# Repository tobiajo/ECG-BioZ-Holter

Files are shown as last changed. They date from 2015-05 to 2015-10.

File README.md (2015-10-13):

# ECG/BioZ Holter (c) by Tobias Johansson

Design and development of a pocket-sized ECG device with respiration monitoring, accelerometer and gyroscope. The produced prototype transmits sampled data with a MCU (PIC24) over Bluetooth to an Android device for which a simple app was developed. To achieve the objective; a system solution was engineered, components chose, PCB designed, soldering done and components programmed or configured.

## Main components

- Texas Instruments ADS1292R
- InvenSense MPU-6050
- Microchip PIC24FJ64GA002
- HC-05 Bluetooth Module

## System overview



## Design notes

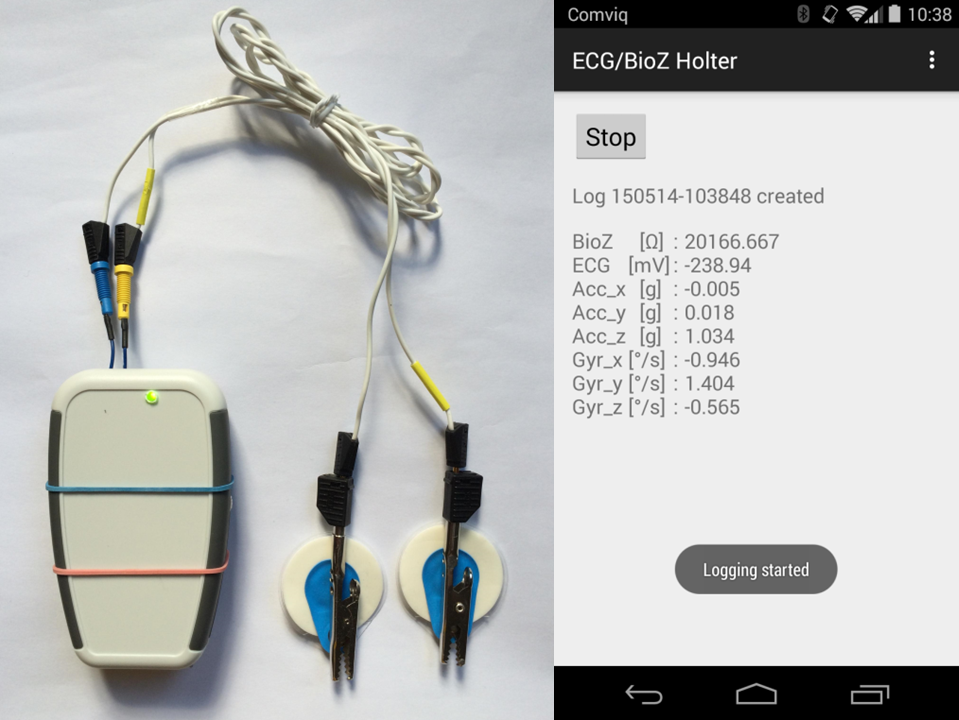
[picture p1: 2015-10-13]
device-and-app.png

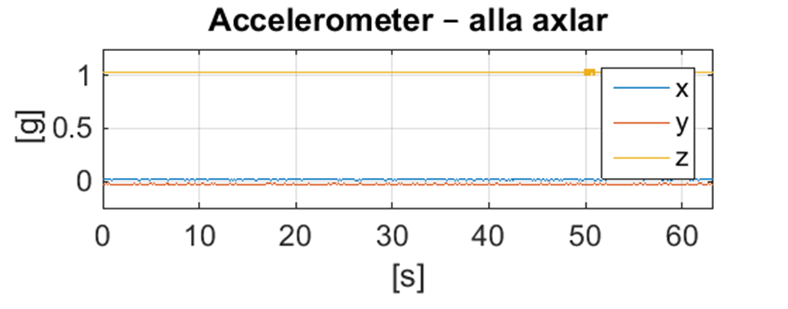
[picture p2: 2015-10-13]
output-plot-accelerometer-fixed.png

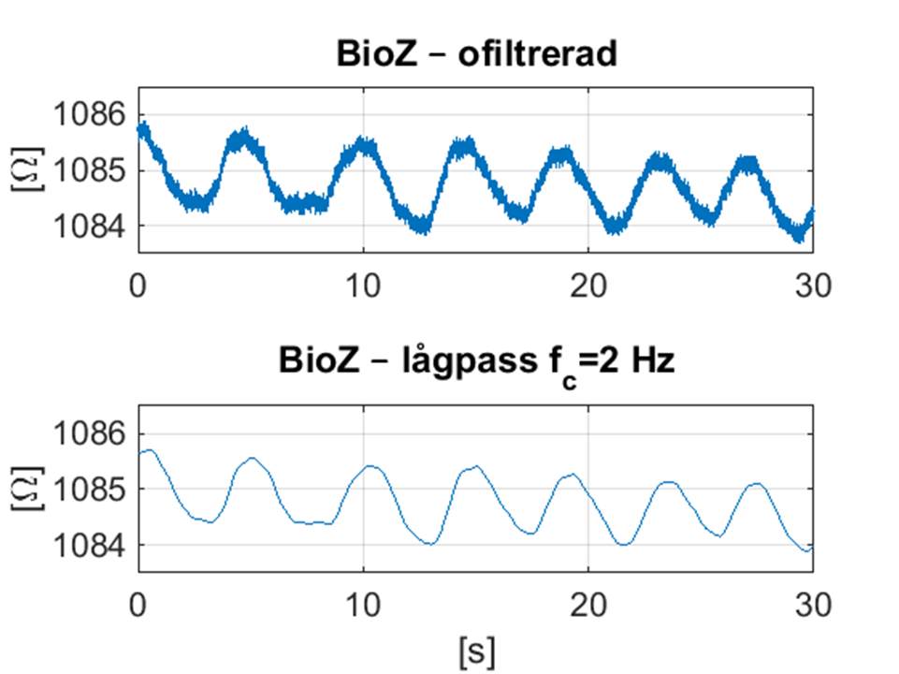
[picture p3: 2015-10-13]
output-plot-respiration-person.png

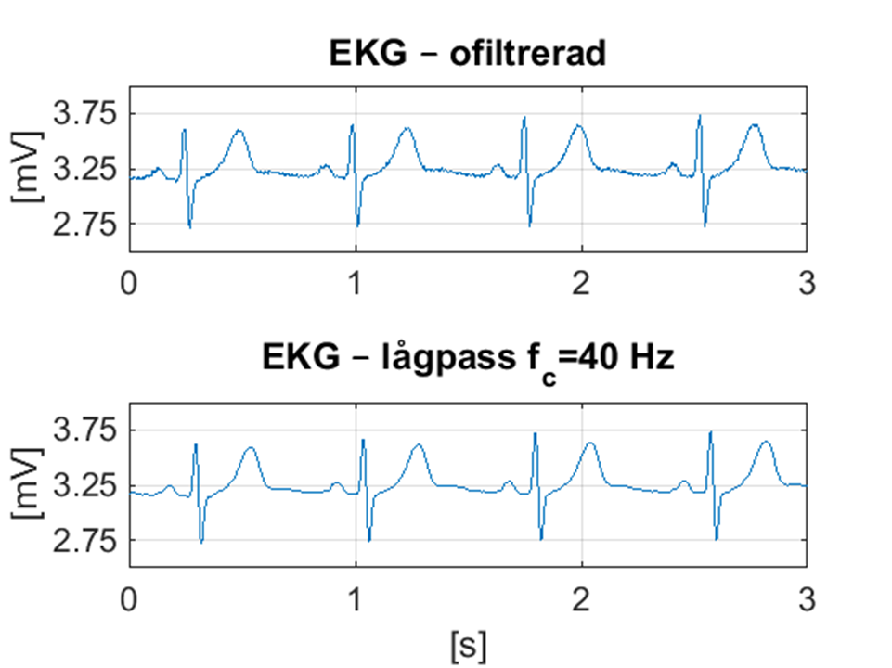
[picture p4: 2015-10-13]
output-plot-ecg-person.png

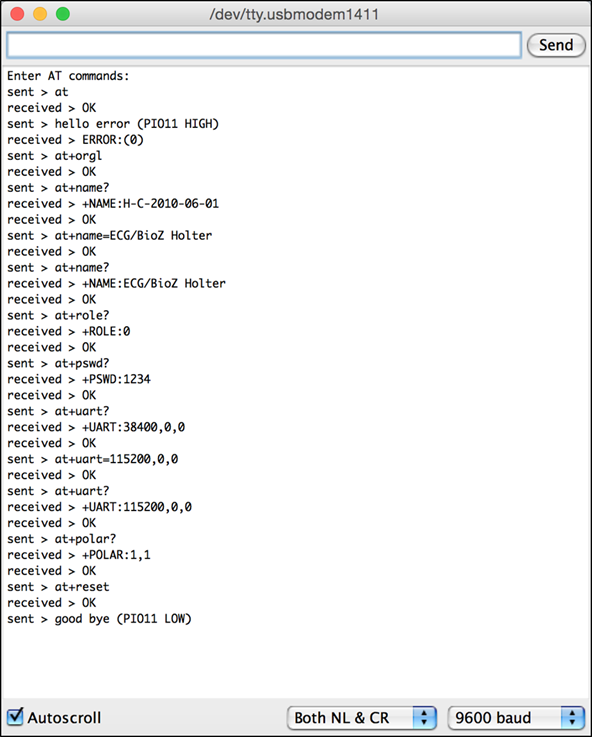
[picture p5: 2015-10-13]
Bluetooth/Arduino/ATSerialMonitorHC05/arduino-config.png

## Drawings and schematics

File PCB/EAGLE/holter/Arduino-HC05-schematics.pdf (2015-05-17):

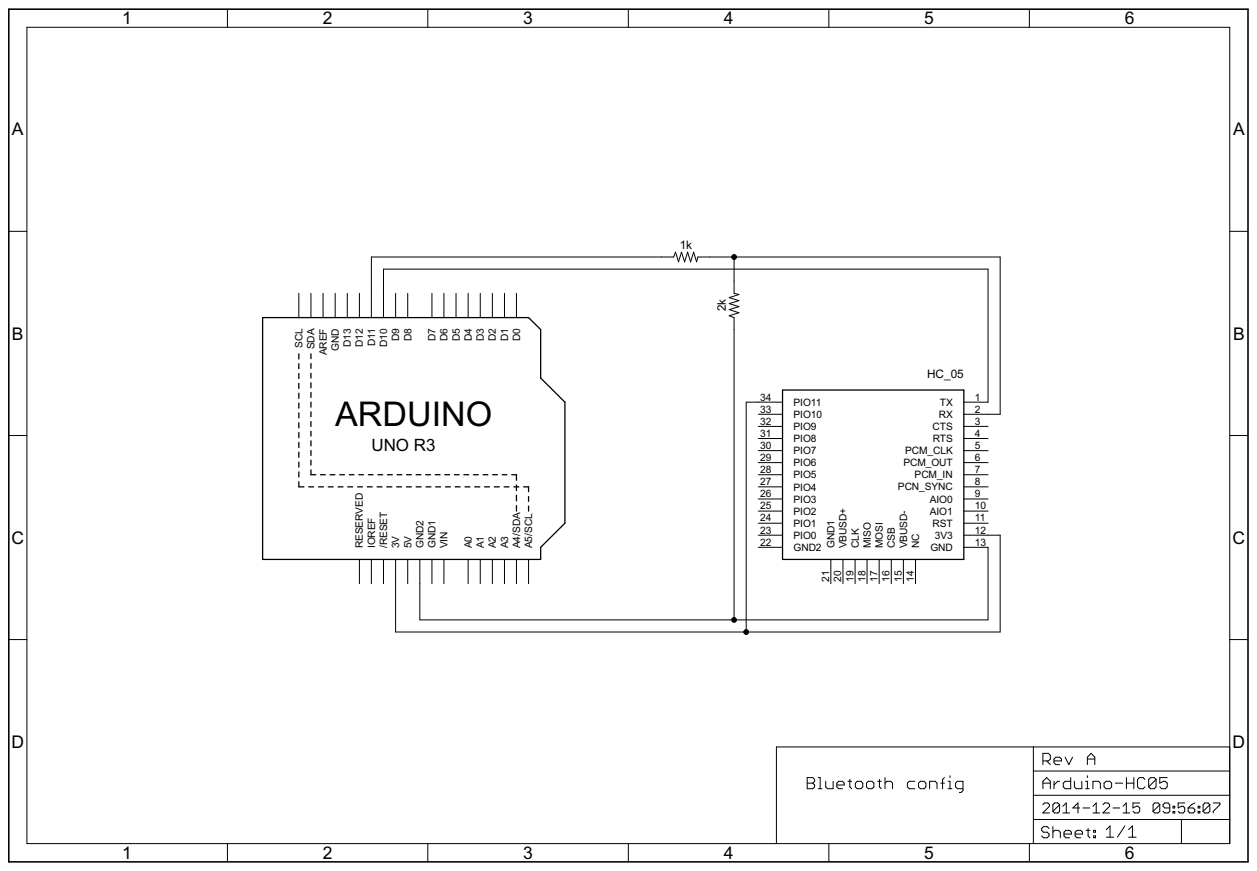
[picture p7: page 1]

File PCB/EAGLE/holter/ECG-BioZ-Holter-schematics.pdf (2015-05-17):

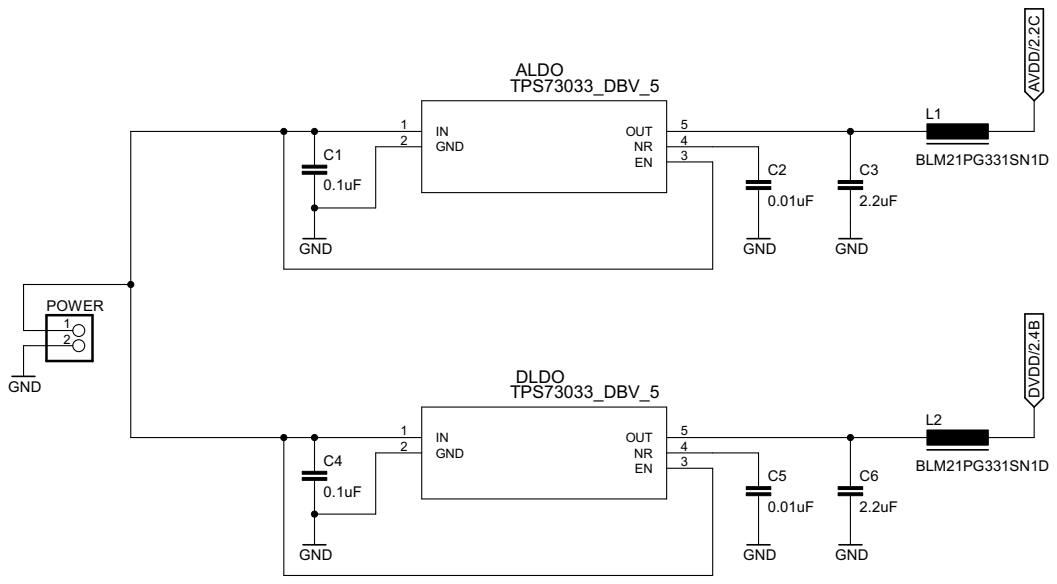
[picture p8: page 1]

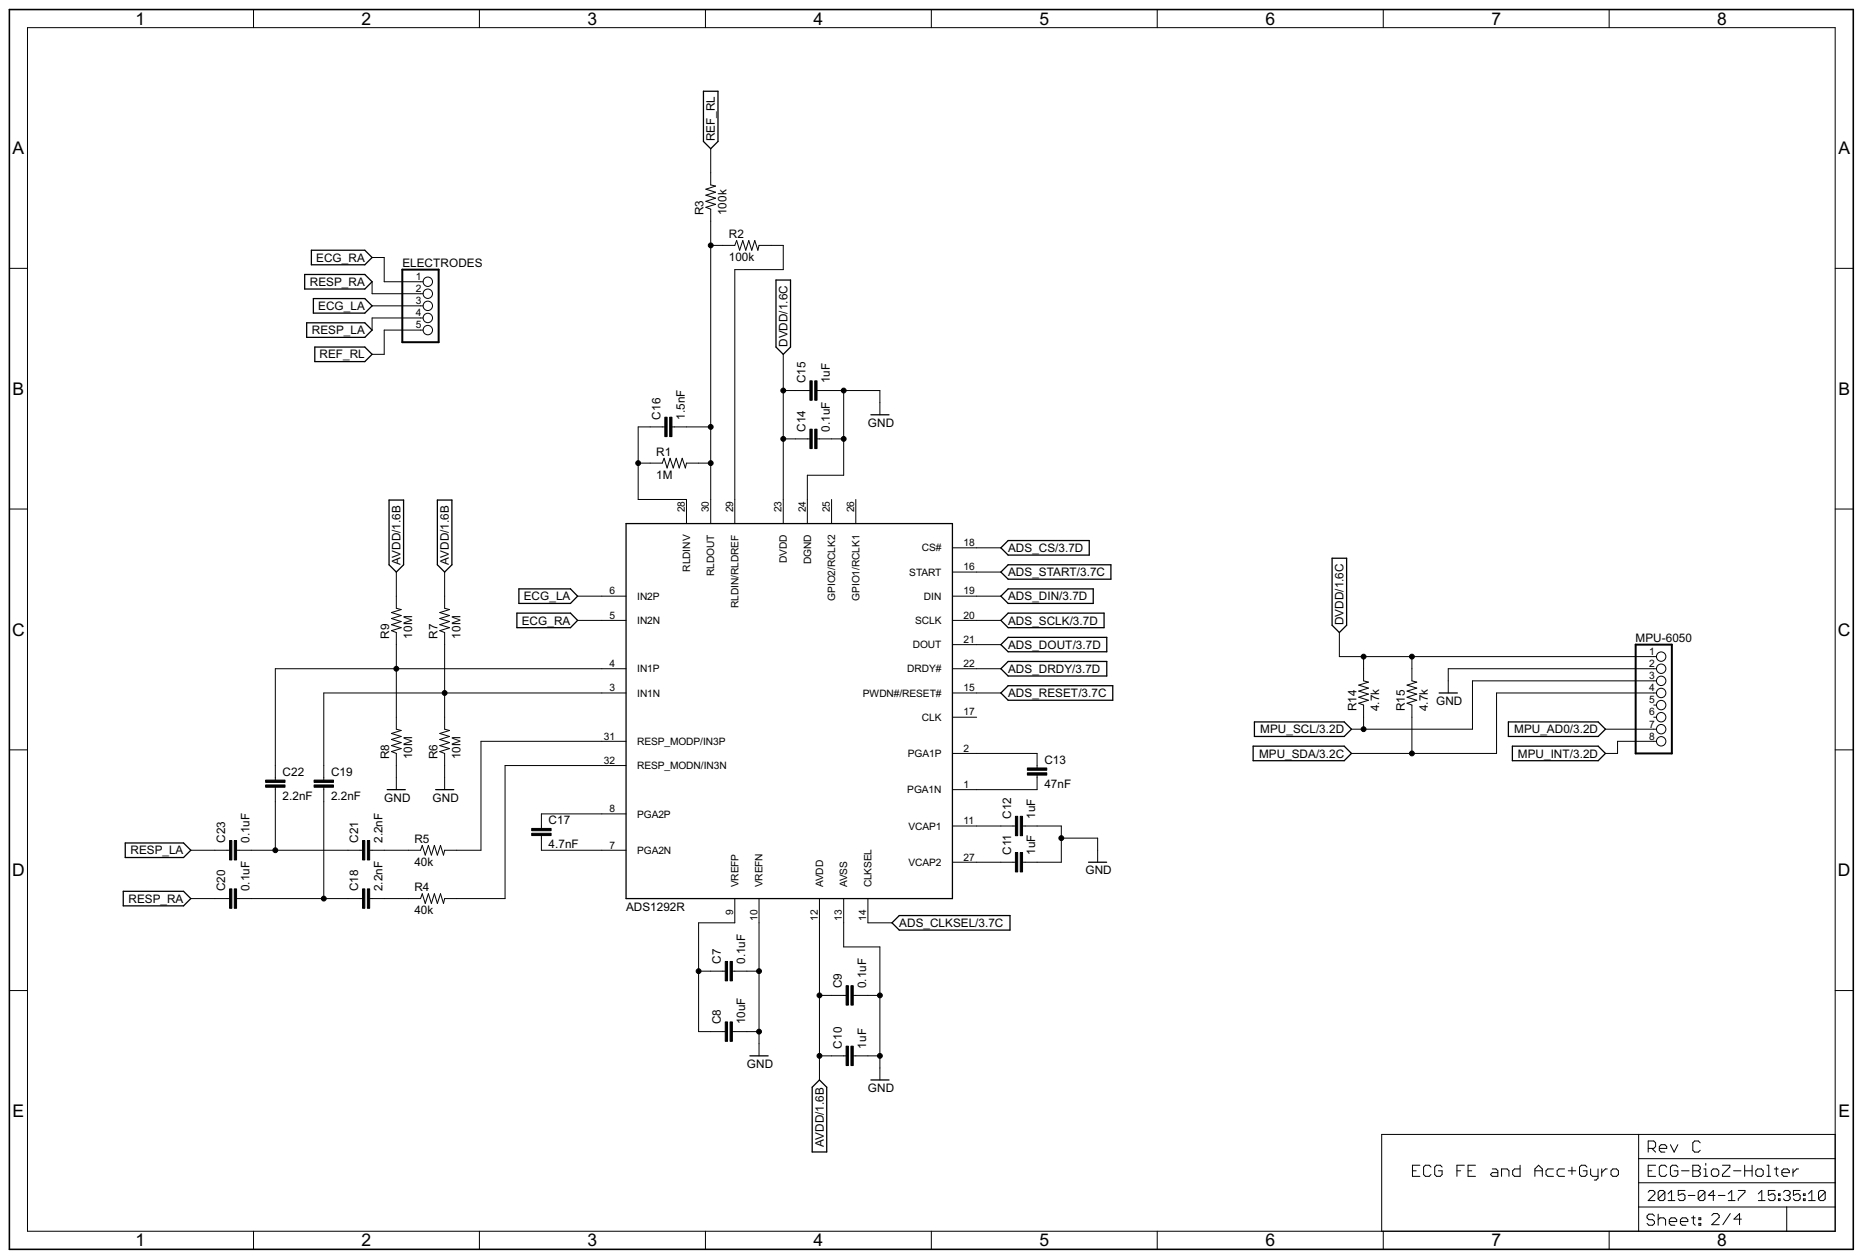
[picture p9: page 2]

0.1uF 10uF GND 0.1uF 1uF GND GND 47nF 1uF 1uF 0.1uF 1uF GND 1M 1.5nF 100k 100k 4.7nF 40k 2.2nF 2.2nF 0.1uF40k 2.2nF 2.2nF 0.1uF 10M GND10M 10M GND10M MPU-6050 GND 4.7k 4.7k AVDD 12 AVSS 13 CLK 17 CLKSEL 14 CS# 18 DGND 24 DIN 19 DOUT 21 DRDY# 22 DVDD 23 GPIO1/RCLK1 26 GPIO2/RCLK2 25 IN1N 3 IN1P 4 IN2N 5 IN2P 6 PGA1N 1 PGA1P 2 PGA2N 7 PGA2P 8 PWDN#/RESET# 15 RESP_MODN/IN3N 32 RESP_MODP/IN3P 31 RLDIN/RLDREF 29 RLDINV 28 RLDOUT 30 SCLK 20 START 16 VCAP1 11 VCAP2 27 VREFN 10 VREFP 9 C7 C8 C9 C10 C13 C11 C12 C14 C15 R1C16 R2 R3 C17 CR4 18 C19 C20 CR5 21 C22 C23 R6 R7 R8 R9 ELECTRODES 12345 12345678 R14 R15 AVDD/1.6B AVDD/1.6B AVDD/1.6B DVDD/1.6C DVDD/1.6C ADS_CLKSEL/3.7C ADS_RESET/3.7C ADS_DRDY/3.7D ADS_DOUT/3.7D ADS_SCLK/3.7D ADS_DIN/3.7D ADS_START/3.7C ADS_CS/3.7D REF_RL REF_RL RESP_RA RESP_RA RESP_LA RESP_LA ECG_LA ECG_LA ECG_RA ECG_RA MPU_SCL/3.2D MPU_SDA/3.2C MPU_AD0/3.2D MPU_INT/3.2D ADS1292R ABCDE 1 2 3 4 5 6 7 8 ABCDE 1 2 3 4 5 6 7 8

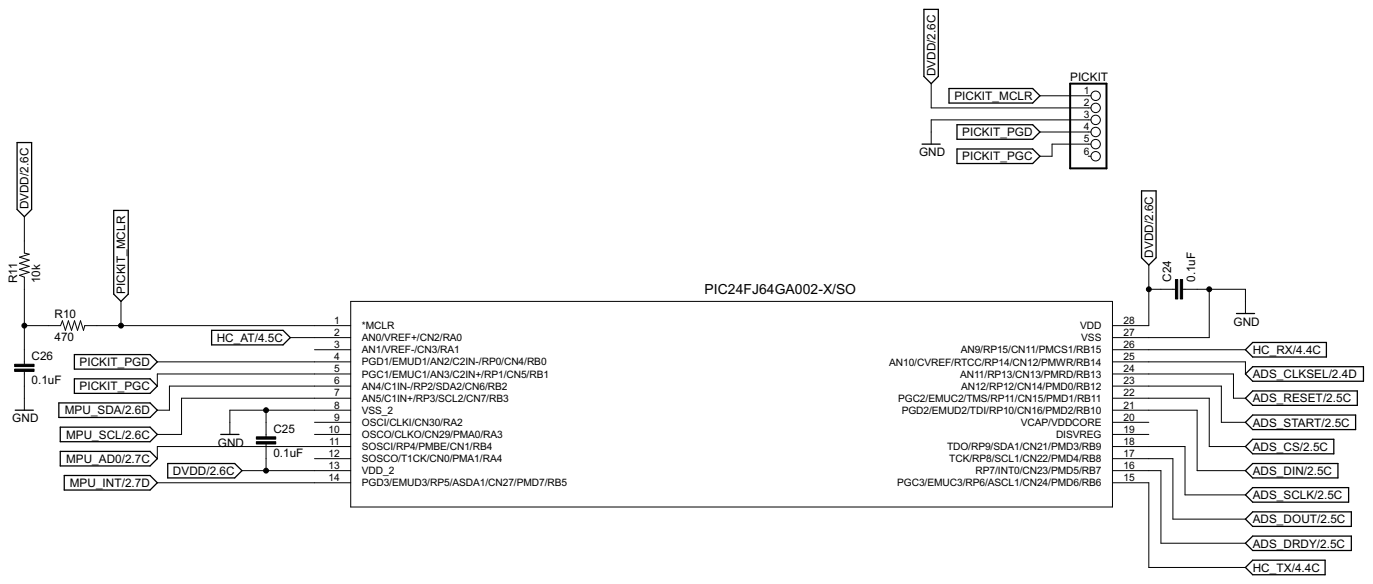
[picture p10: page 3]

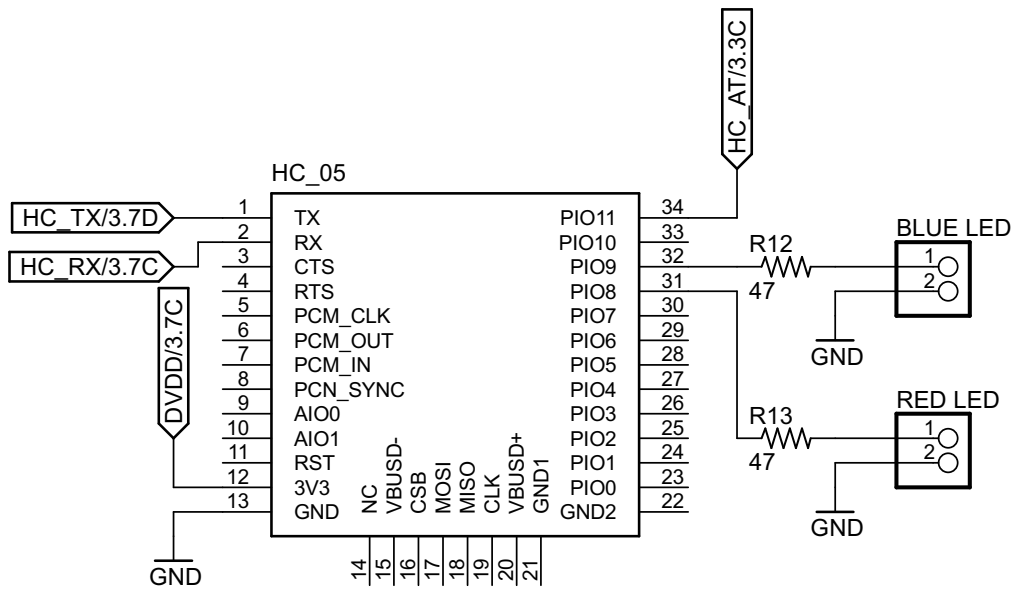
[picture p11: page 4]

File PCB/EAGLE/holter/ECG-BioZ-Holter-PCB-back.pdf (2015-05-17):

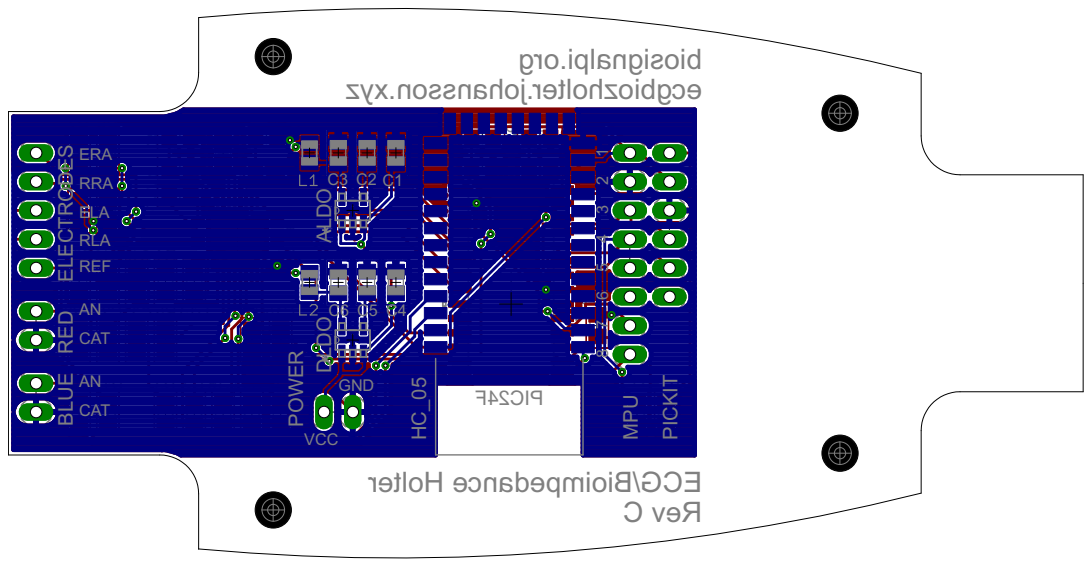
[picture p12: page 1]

CAT

GND

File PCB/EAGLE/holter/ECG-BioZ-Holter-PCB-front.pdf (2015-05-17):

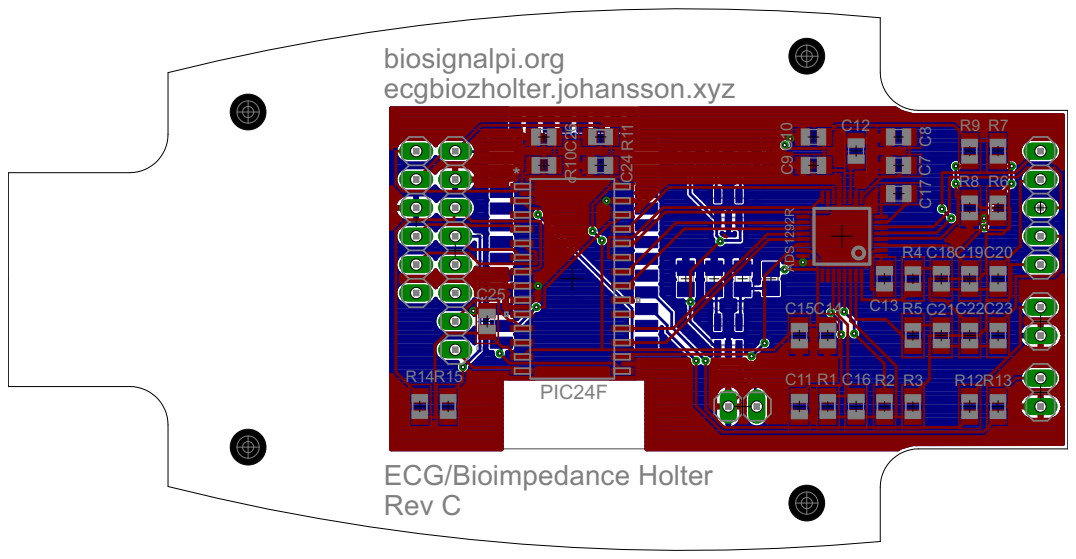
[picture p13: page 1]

PIC24F | C11 R1 | C16 R2 | R3

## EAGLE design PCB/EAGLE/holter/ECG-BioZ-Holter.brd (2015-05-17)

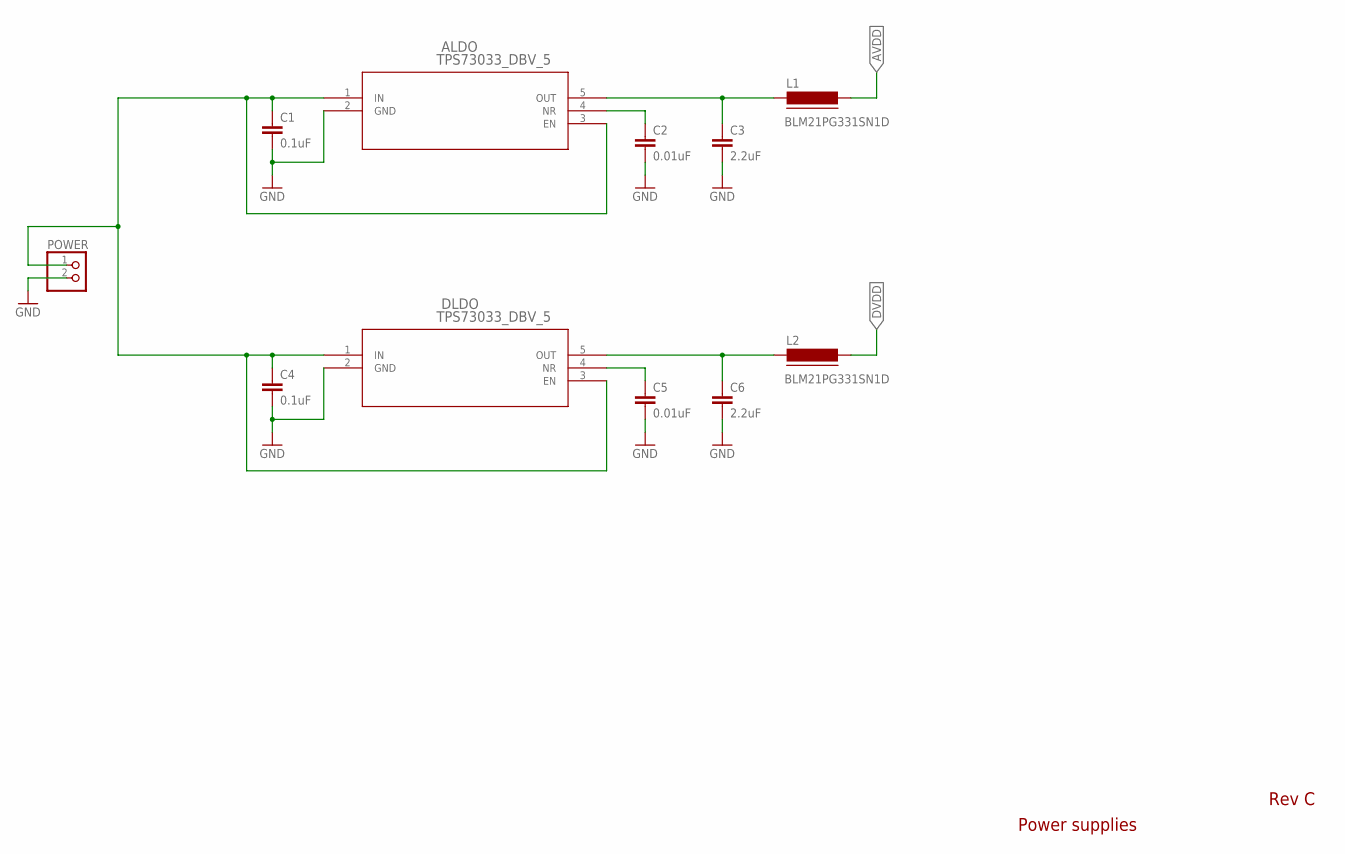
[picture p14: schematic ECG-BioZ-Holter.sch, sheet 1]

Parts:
ALDO: TPS73033_DBV_5; DBV5
C1, C4: 0.1uF; C0805
C2, C5: 0.01uF; C0805
C3, C6: 2.2uF; C0805
DLDO: TPS73033_DBV_5; DBV5
L1, L2: BLM21PG331SN1D; FB805
POWER: PINHD-1X2; 1X02

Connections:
AVDD: L1.2; also elsewhere on the board
DVDD: L2.2; also elsewhere on the board
GND: ALDO.2 (GND), C1.2, C2.2, C3.2, C4.2, C5.2, C6.2, DLDO.2 (GND), POWER.2; also elsewhere on the board
unnamed: ALDO.1 (IN), ALDO.3 (EN), C1.1, C4.1, DLDO.1 (IN), DLDO.3 (EN), POWER.1
unnamed: C5.1, DLDO.4 (NR)
unnamed: ALDO.4 (NR), C2.1
unnamed: ALDO.5 (OUT), C3.1, L1.1
unnamed: C6.1, DLDO.5 (OUT), L2.1

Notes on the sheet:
Rev C
Power supplies

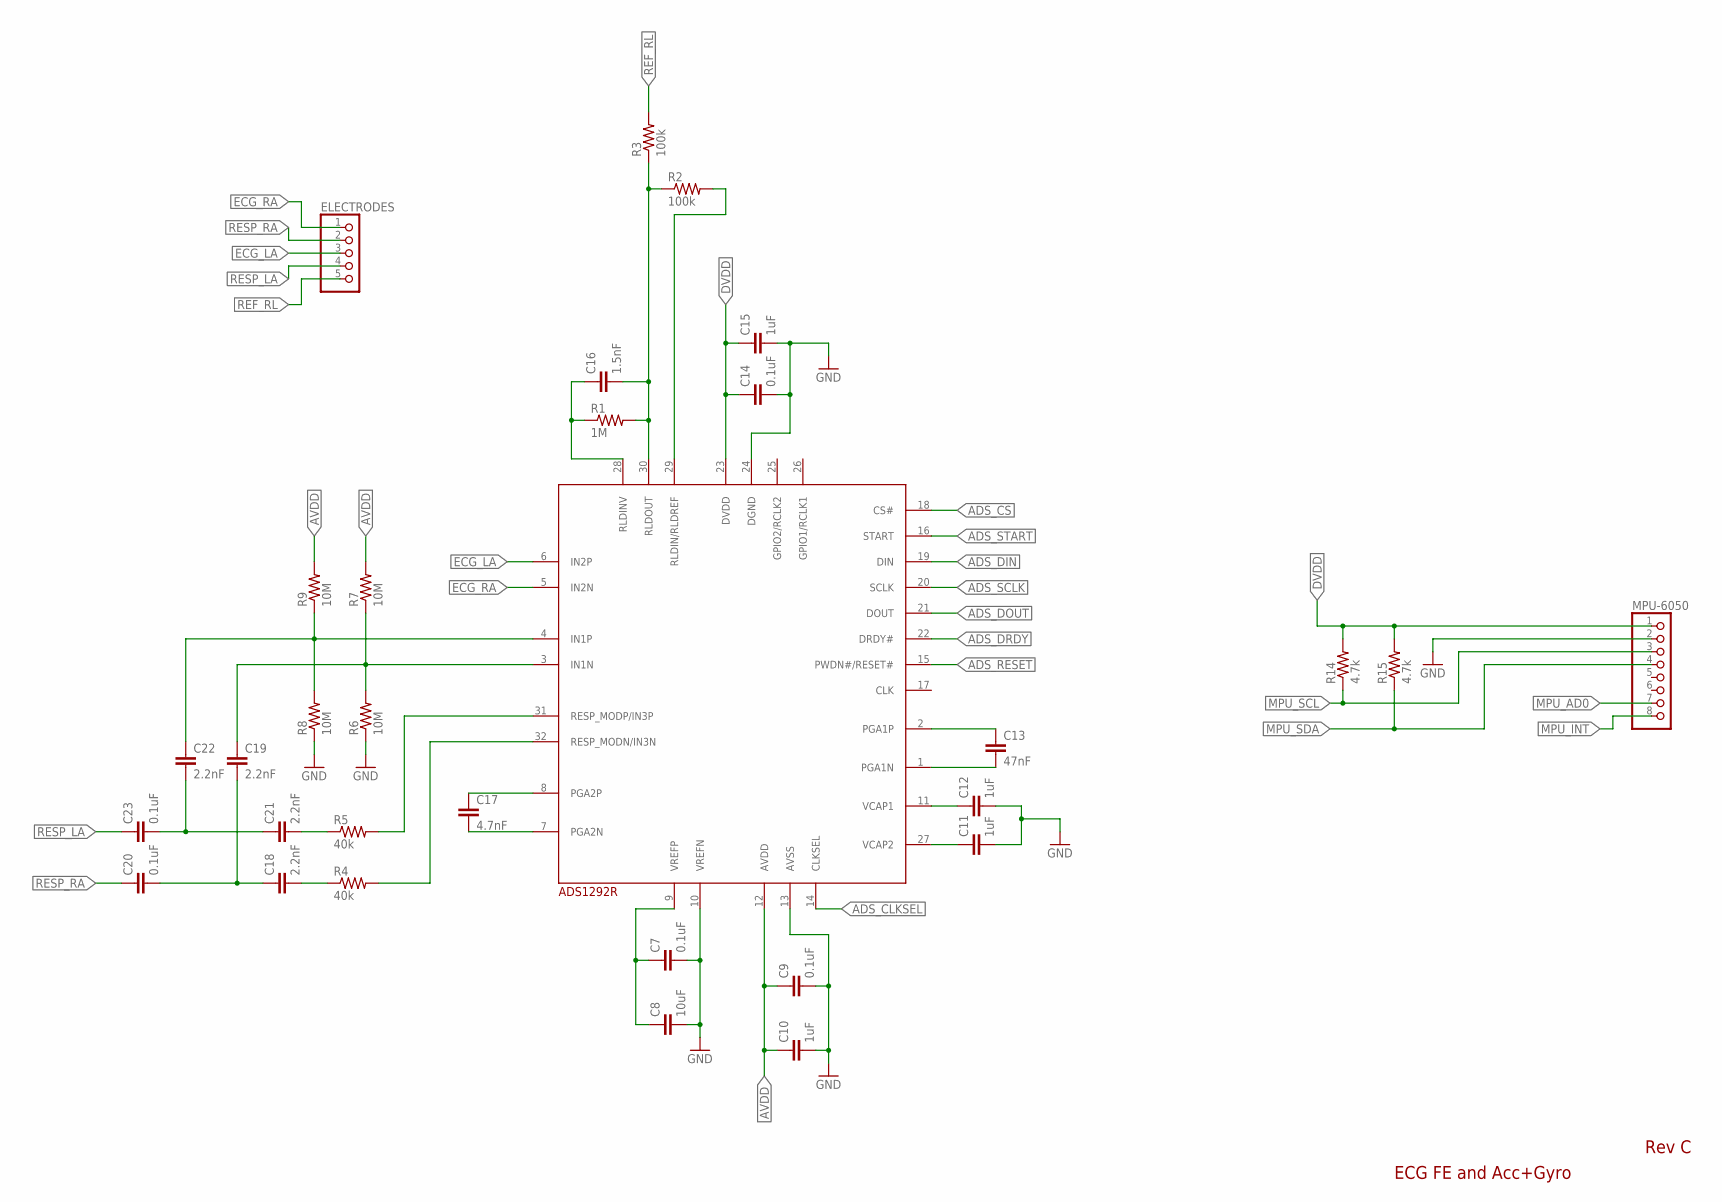
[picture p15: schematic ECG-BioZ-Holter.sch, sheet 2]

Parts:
ADS1292R: ADS1292R; TQFP-32
C7, C9, C14, C20, C23: 0.1uF; C0805
C8: 10uF; C0805
C10, C11, C12, C15: 1uF; C0805
C13: 47nF; C0805
C16: 1.5nF; C0805
C17: 4.7nF; C0805
C18, C19, C21, C22: 2.2nF; C0805
ELECTRODES: PINHD-1X5; 1X05
MPU: MPU-6050; 1X08
R1: 1M; R0805
R2, R3: 100k; R0805
R4, R5: 40k; R0805
R6, R7, R8, R9: 10M; R0805
R14, R15: 4.7k; R0805

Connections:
ADS_CLKSEL: ADS1292R.14 (CLKSEL); also elsewhere on the board
ADS_CS: ADS1292R.18 (CS#); also elsewhere on the board
ADS_DIN: ADS1292R.19 (DIN); also elsewhere on the board
ADS_DOUT: ADS1292R.21 (DOUT); also elsewhere on the board
ADS_DRDY: ADS1292R.22 (DRDY#); also elsewhere on the board
ADS_RESET: ADS1292R.15 (PWDN#/RESET#); also elsewhere on the board
ADS_SCLK: ADS1292R.20 (SCLK); also elsewhere on the board
ADS_START: ADS1292R.16 (START); also elsewhere on the board
AVDD: ADS1292R.12 (AVDD), C9.1, C10.1, R7.2, R9.2; also elsewhere on the board
DVDD: ADS1292R.23 (DVDD), C14.1, C15.1, MPU.1, R14.2, R15.2; also elsewhere on the board
ECG_LA: ADS1292R.6 (IN2P), ELECTRODES.3
ECG_RA: ADS1292R.5 (IN2N), ELECTRODES.1
GND: ADS1292R.10 (VREFN), ADS1292R.13 (AVSS), ADS1292R.24 (DGND), C7.2, C8.2, C9.2, C10.2, C11.2, C12.2, C14.2, C15.2, MPU.2, R6.1, R8.1; also elsewhere on the board
MPU_AD0: MPU.7; also elsewhere on the board
MPU_INT: MPU.8; also elsewhere on the board
MPU_SCL: MPU.3, R14.1; also elsewhere on the board
MPU_SDA: MPU.4, R15.1; also elsewhere on the board
unnamed: ADS1292R.11 (VCAP1), C12.1
unnamed: ADS1292R.9 (VREFP), C7.1, C8.1
unnamed: ADS1292R.27 (VCAP2), C11.1
unnamed: ADS1292R.2 (PGA1P), C13.1
unnamed: ADS1292R.1 (PGA1N), C13.2
unnamed: ADS1292R.30 (RLDOUT), C16.2, R1.2, R2.1, R3.1
unnamed: ADS1292R.28 (RLDINV), C16.1, R1.1
unnamed: ADS1292R.29 (RLDIN/RLDREF), R2.2
unnamed: ADS1292R.8 (PGA2P), C17.1
unnamed: ADS1292R.7 (PGA2N), C17.2
unnamed: ADS1292R.32 (RESP_MODN/IN3N), R4.2
unnamed: C18.2, R4.1
unnamed: C18.1, C19.2, C20.2
unnamed: ADS1292R.3 (IN1N), C19.1, R6.2, R7.1
unnamed: ADS1292R.31 (RESP_MODP/IN3P), R5.2
unnamed: C21.2, R5.1
unnamed: C21.1, C22.2, C23.2
unnamed: ADS1292R.4 (IN1P), C22.1, R8.2, R9.1
REF_RL: ELECTRODES.5, R3.2
RESP_LA: C23.1, ELECTRODES.4
RESP_RA: C20.1, ELECTRODES.2

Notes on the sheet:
Rev C
ECG FE and Acc+Gyro

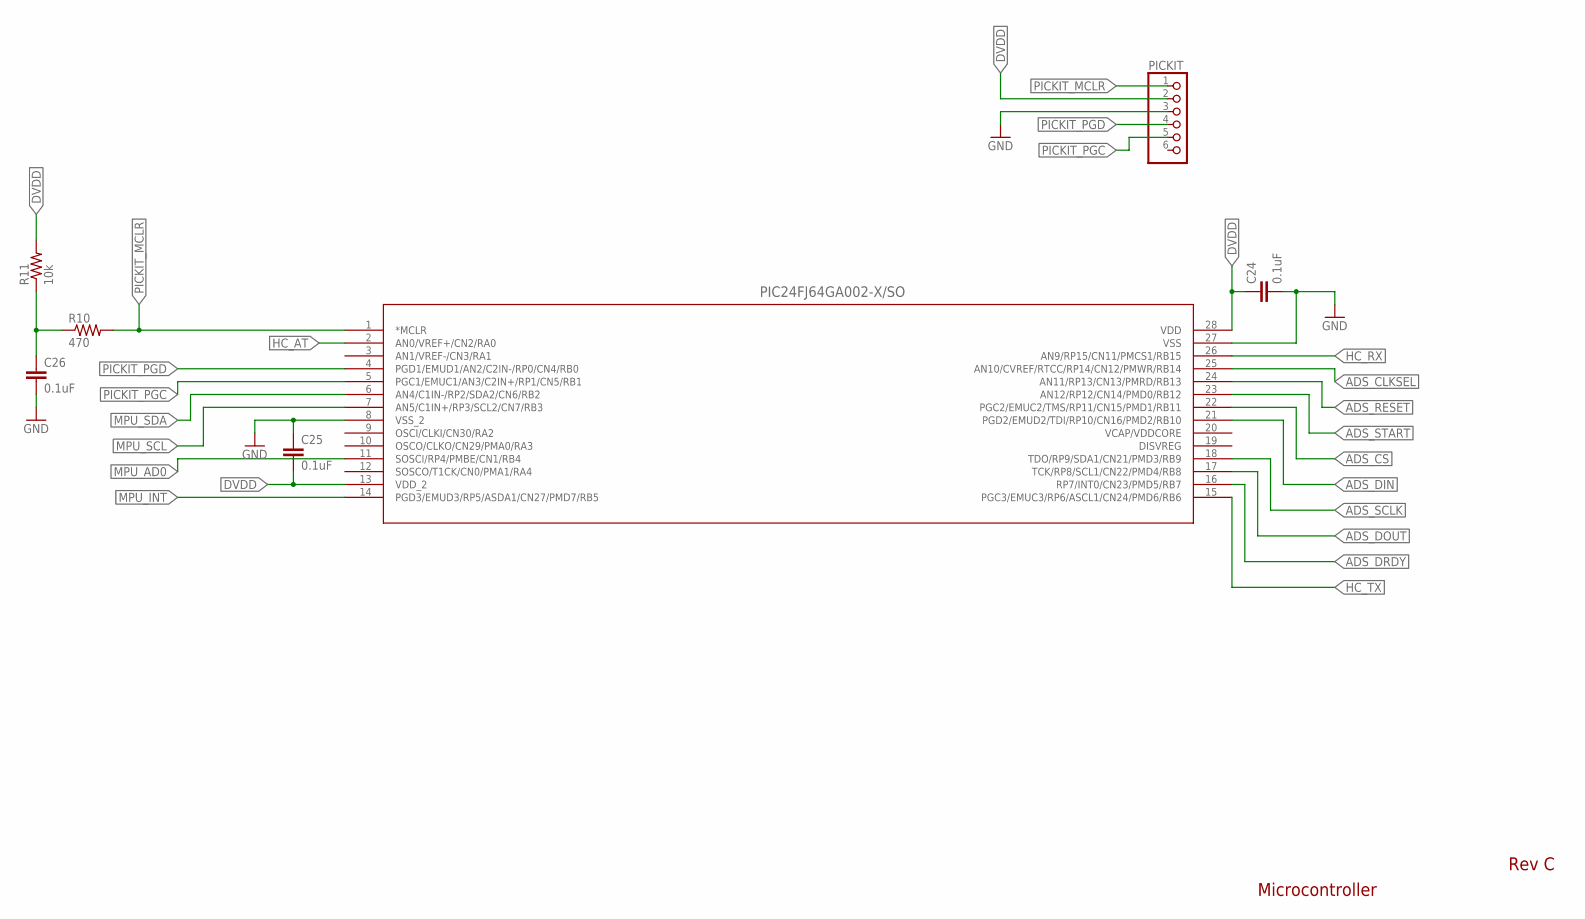
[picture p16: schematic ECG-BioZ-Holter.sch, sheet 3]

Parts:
C24, C25, C26: 0.1uF; C0805
PIC24F: PIC24FJ64GA002-X/SO; SOIC28-W_MC
PICKIT: PINHD-1X6; 1X06
R10: 470; R0805
R11: 10k; R0805

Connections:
ADS_CLKSEL: PIC24F.25 (AN10/CVREF/RTCC/RP14/CN12/PMWR/RB14); also elsewhere on the board
ADS_CS: PIC24F.22 (PGC2/EMUC2/TMS/RP11/CN15/PMD1/RB11); also elsewhere on the board
ADS_DIN: PIC24F.21 (PGD2/EMUD2/TDI/RP10/CN16/PMD2/RB10); also elsewhere on the board
ADS_DOUT: PIC24F.17 (TCK/RP8/SCL1/CN22/PMD4/RB8); also elsewhere on the board
ADS_DRDY: PIC24F.16 (RP7/INT0/CN23/PMD5/RB7); also elsewhere on the board
ADS_RESET: PIC24F.24 (AN11/RP13/CN13/PMRD/RB13); also elsewhere on the board
ADS_SCLK: PIC24F.18 (TDO/RP9/SDA1/CN21/PMD3/RB9); also elsewhere on the board
ADS_START: PIC24F.23 (AN12/RP12/CN14/PMD0/RB12); also elsewhere on the board
DVDD: C24.1, C25.2, PIC24F.13 (VDD_2), PIC24F.28 (VDD), PICKIT.2, R11.2; also elsewhere on the board
GND: C24.2, C25.1, C26.2, PIC24F.8 (VSS_2), PIC24F.27 (VSS), PICKIT.3; also elsewhere on the board
HC_AT: PIC24F.2 (AN0/VREF+/CN2/RA0); also elsewhere on the board
HC_RX: PIC24F.26 (AN9/RP15/CN11/PMCS1/RB15); also elsewhere on the board
HC_TX: PIC24F.15 (PGC3/EMUC3/RP6/ASCL1/CN24/PMD6/RB6); also elsewhere on the board
MPU_AD0: PIC24F.11 (SOSCI/RP4/PMBE/CN1/RB4); also elsewhere on the board
MPU_INT: PIC24F.14 (PGD3/EMUD3/RP5/ASDA1/CN27/PMD7/RB5); also elsewhere on the board
MPU_SCL: PIC24F.7 (AN5/C1IN+/RP3/SCL2/CN7/RB3); also elsewhere on the board
MPU_SDA: PIC24F.6 (AN4/C1IN-/RP2/SDA2/CN6/RB2); also elsewhere on the board
unnamed: C26.1, R10.1, R11.1
PICKIT_MCLR: PIC24F.1 (*MCLR), PICKIT.1, R10.2
PICKIT_PGC: PIC24F.5 (PGC1/EMUC1/AN3/C2IN+/RP1/CN5/RB1), PICKIT.5
PICKIT_PGD: PIC24F.4 (PGD1/EMUD1/AN2/C2IN-/RP0/CN4/RB0), PICKIT.4

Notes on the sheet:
Rev C
Microcontroller

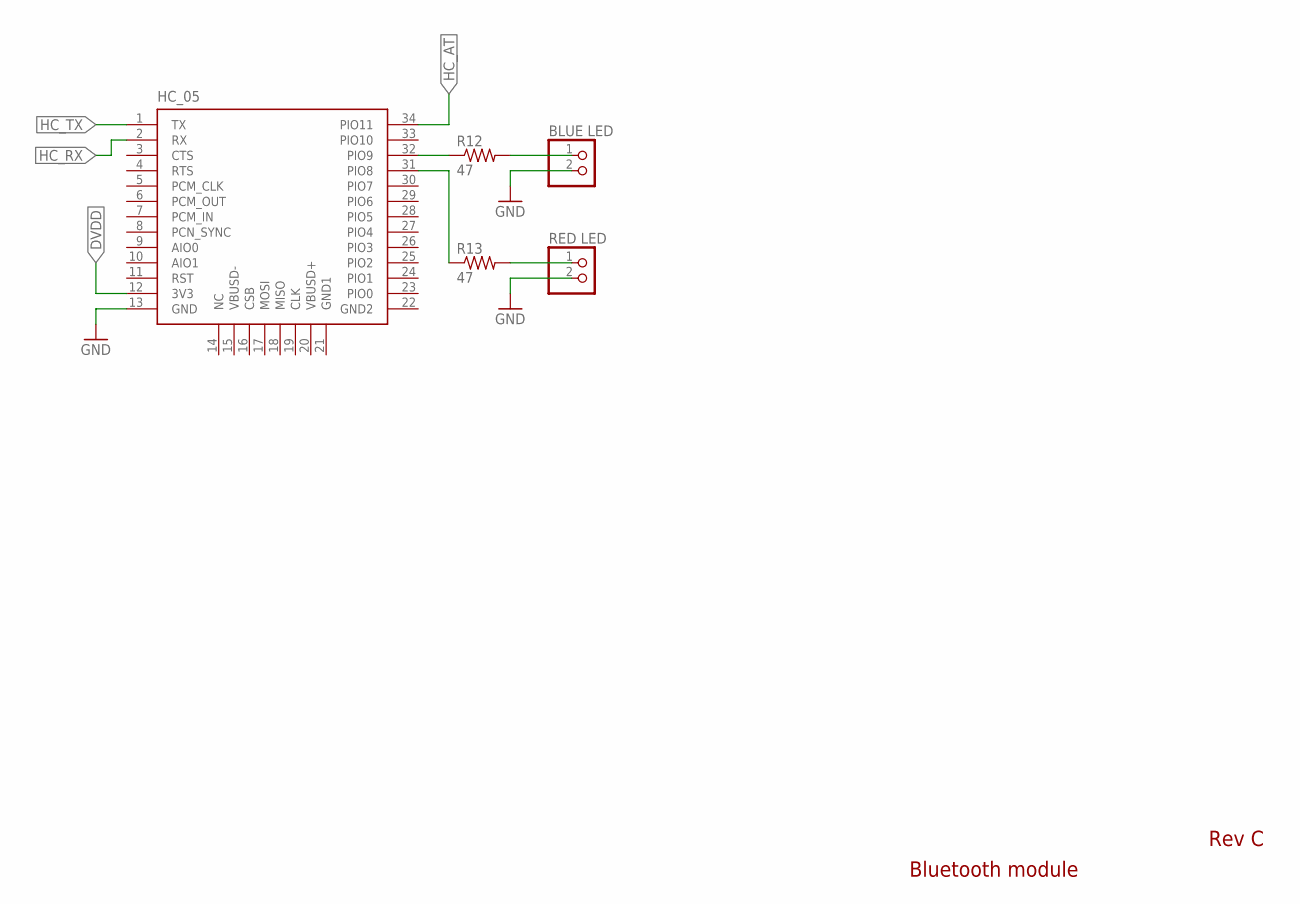
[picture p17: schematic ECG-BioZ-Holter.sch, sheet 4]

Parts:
BLUE: BLUE LED; 1X02
HC_05: HC_05; BLUETOOTH_SMD
R12, R13: 47; R0805
RED: RED LED; 1X02

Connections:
DVDD: HC_05.12 (3V3); also elsewhere on the board
GND: BLUE.2, HC_05.13 (GND), RED.2; also elsewhere on the board
HC_AT: HC_05.34 (PIO11); also elsewhere on the board
HC_RX: HC_05.2 (RX); also elsewhere on the board
HC_TX: HC_05.1 (TX); also elsewhere on the board
unnamed: HC_05.32 (PIO9), R12.1
unnamed: BLUE.1, R12.2
unnamed: HC_05.31 (PIO8), R13.1
unnamed: R13.2, RED.1

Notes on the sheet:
Rev C
Bluetooth module

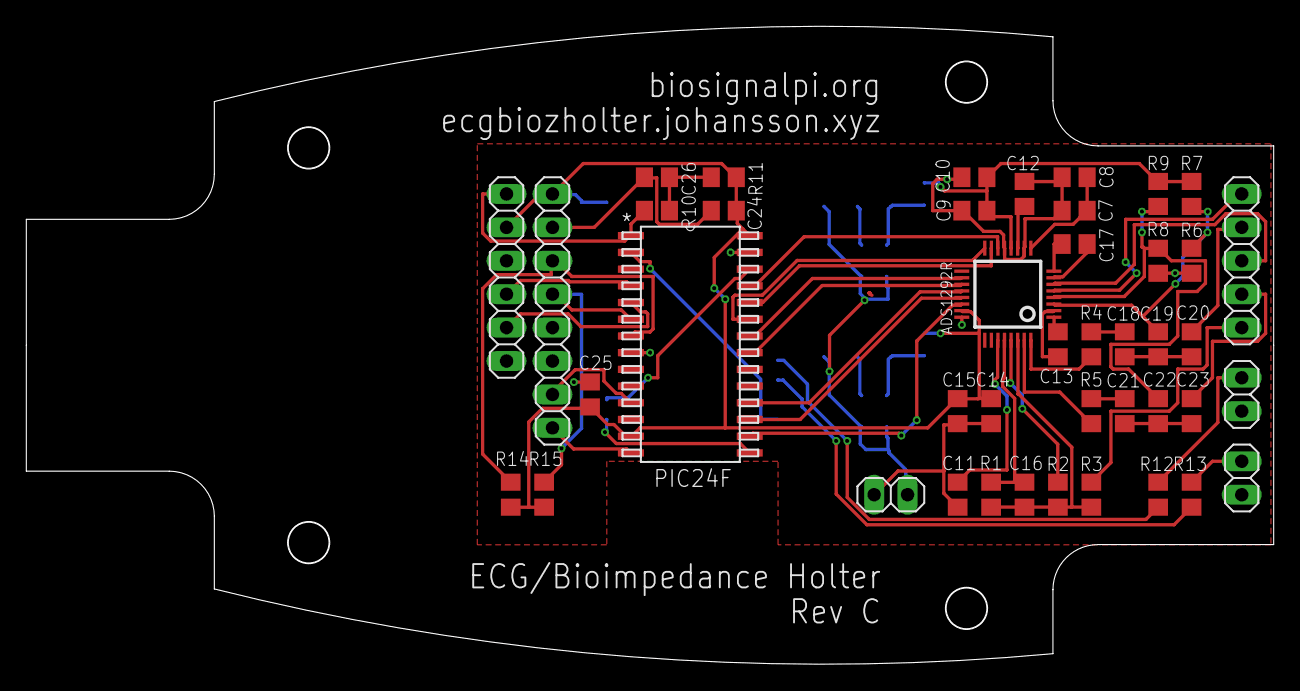
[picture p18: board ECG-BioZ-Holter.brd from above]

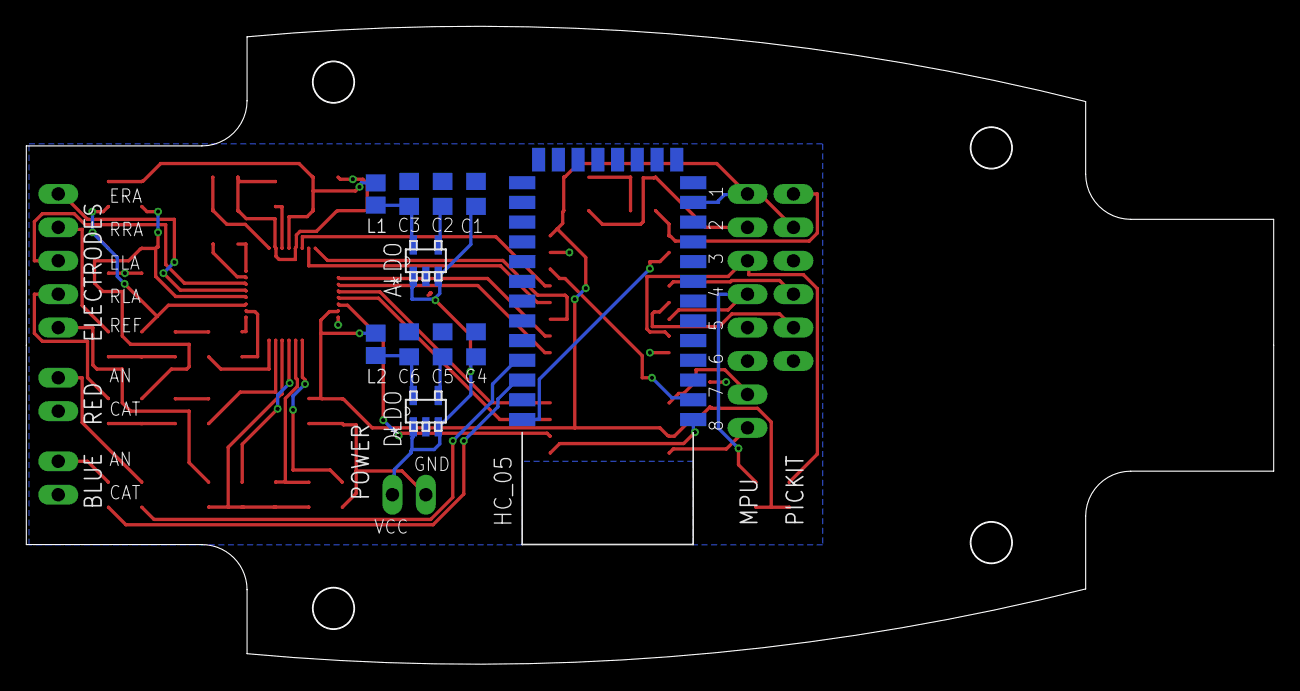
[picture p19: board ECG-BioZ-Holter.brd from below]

Board: 2 copper layers, 94.8 x 48.5 mm, 54 parts (11 on the bottom side), 54 nets.

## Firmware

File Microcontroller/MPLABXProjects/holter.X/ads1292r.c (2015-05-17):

/*
 * File:    ads1292r.c
 * Project: ecgbiozholter.johansson.xyz
 * MCU:     Microchip PIC24FJ64GA002
 * Author:  Tobias Johansson
 * Version: 1.3, 23 Apr 2015
 */

#include "ads1292r.h"

#define RIGHT_LEG_DRIVE 1 // set 1 for enable RLD, otherwise disabled

// Initialization.
void ads1292r_init(void) {
    // Pin directions
    TRISBbits.TRISB14 = 0; // ADS_CLKSEL = out
    TRISBbits.TRISB13 = 0; // ADS_RESET  = out
    TRISBbits.TRISB12 = 0; // ADS_START  = out
    TRISBbits.TRISB11 = 0; // ADS_CS     = out
    TRISBbits.TRISB7  = 1; // ADS_DRDY   = in

    // Power-Up Settings
    LATBbits.LATB14 = 1; // internal clock
    LATBbits.LATB13 = 1; // no: reset
    LATBbits.LATB12 = 1; // start
    LATBbits.LATB11 = 1; // no: chip select

    // PPS SPI2
    PPSInput (PPS_SDI2, PPS_RP8);     // ADS_DOUT
    PPSOutput(PPS_RP9,  PPS_SCK2OUT); // ADS_SCLK
    PPSOutput(PPS_RP10, PPS_SDO2);    // ADS_DIN

    // SPI2 init
    // "If SCLK is 1 MHz, one byte is transferred in 8 µs. Because this transfer
    // time exceeds the t_SDECODE specification, the processor can send
    // subsequent bytes without delay." - Data sheet p. 37
    SPI2CON1 = 0x003D; // Master Mode, SPI clock = 1000 kHz (Fcy = 16 MHz)
    SPI2STAT = 0x8000; // Enables module

    // Delay for Power-On Reset and Oscillator Start-Up
    __delay_ms(1000);

    // "The internal oscillator generates a 512-kHz clock." - Data sheet p. 16
    // "f_MOD = f_CLK / 4 (default, use when f_CLK = 512 kHz)" - Data sheet. 47
    // => t_MOD = 7.8125 us, t_CLK = 1.953125 us

    // Issue Reset Pulse then Wait for 18 t_CLKs
    LATBbits.LATB13 = 0;
    __delay_us(8);  // Reset low width min = 1 t_MOD
    LATBbits.LATB13 = 1;
    __delay_us(36); // Recommended wait after reset = 18 t_CLK
	
    // "After releasing RESET, the configuration register must be programmed..."
    // - Data sheet p. 62

    // Device Wakes Up in RDATAC Mode, so Send
    // SDATAC Command so Registers can be Written
    ads1292r_command(ADS1292R_CMD_SDATAC);

    ads1292r_config();

    // Activate Conversion
    LATBbits.LATB12 = 1; // START = 1

    // Put the Device Back in RDATAC Mode
    ads1292r_command(ADS1292R_CMD_RDATAC);
}

// Configuration settings.
void ads1292r_config(void) {
    // Continuous conversion, Data Rate = 1 kSPS
    ads1292r_wreg(ADS1292R_REG_CONFIG1, 0x03);

    // Reference buffer is enabled
    ads1292r_wreg(ADS1292R_REG_CONFIG2, 0xA0);

    // Channel 1 PGA gain = 4, Normal electrode input
    ads1292r_wreg(ADS1292R_REG_CH1SET, 0x40);

    // Channel 2 PGA gain = 4, Normal electrode input
    ads1292r_wreg(ADS1292R_REG_CH2SET, 0x40);

    // Chop frequency = f_MOD/16, RLD buffer is enabled if RIGHT_LEG_DRIVE == 1
    #if RIGHT_LEG_DRIVE == 1
    #define RLD_BIT 0x20
    #else
    #define RLD_BIT 0x00
    #endif
    ads1292r_wreg(ADS1292R_REG_RLD_SENS, 0x00 | RLD_BIT);

    // CLK_DIV bit of LOFF_STAT register = 0 by default

    // Enables respiration circuits, Respiration phase = 112.5°
    // "It can be noted that gain = 4 and phase = 112.5° yield the best
    // performance..." - Data sheet p. 59
    ads1292r_wreg(ADS1292R_REG_RESP1, 0xEA);

    // Resp frequency, 32 kHz, RLDREF signal (AVDD-AVSS)/2 generated internally
    ads1292r_wreg(ADS1292R_REG_RESP2, 0x03);
}

//------------------------------------------------------------------------------
// Basic Functions

// Transfer data bidirectional.
UINT8 ads1292r_transfer(UINT8 data) {
    SPI2BUF = data;               // write to buffer
    while (!SPI2STATbits.SPIRBF); // wait transfer
    return SPI2BUF;               // read received
}

// Set chip select low.
void ads1292r_cs_low(void) {
    LATBbits.LATB11 = 0;
}

// Set chip select high.
void ads1292r_cs_high(void) {
    // "Always wait four or more t_CLK cycles before taking CS high."
    // - Data sheet p. 28
    __delay_us(8);
    LATBbits.LATB11 = 1;
}

//------------------------------------------------------------------------------
// Putting it Together

// Sends a command.
void ads1292r_command(UINT8 cmd) {
    ads1292r_cs_low();
    ads1292r_transfer(cmd);
    ads1292r_cs_high();
}

// Reads from a register.
UINT8 ads1292r_rreg(UINT8 reg) {
    UINT8 value;
    ads1292r_cs_low();

    ads1292r_transfer(ADS1292R_CMD_RREG | reg);
    ads1292r_transfer(0x00); // [number of registers to be read]-1 = 0x00
    value = ads1292r_transfer(ADS1292R_CMD_DUMMY);

    ads1292r_cs_high();
    return value;
}

// Writes to a register.
void ads1292r_wreg(UINT8 reg, UINT8 value) {
    ads1292r_cs_low();

    ads1292r_transfer(ADS1292R_CMD_WREG | reg);
    ads1292r_transfer(0x00); // [number of registers to be written]-1 = 0x00
    ads1292r_transfer(value);

    ads1292r_cs_high();
}

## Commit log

2015-05-17 Add schematics
    [Arduino-HC05.sch, ECG-BioZ-Holter.brd, ECG-BioZ-Holter.sch]
2015-10-13 Add prototype pictures
